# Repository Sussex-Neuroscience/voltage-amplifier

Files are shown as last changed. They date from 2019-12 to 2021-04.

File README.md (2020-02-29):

# Arduino Due compatible voltage amplifier

Hi! This repository contains all the necessary documents to replicate an arduino Due compatible voltage amplifier.

This system was developed as part of a research project of the [Ward Lab](http://www.sussex.ac.uk/profiles/92444/research). It is to be used with a stimulus isolation adaptor from BIOPAC, more specifically one of the models that provide isolated voltage: https://www.biopac.com/product/stimulus-isolation-adapters/

The idea is simple, we use the true analog output ports from the Arduino DUE as an independent channel and amplify their signals using Operational amplifiers. In this case two [LM741](https://www.biopac.com/product/stimulus-isolation-adapters/) from Texas instruments. Using serial communication the system can be controlled in various ways, from the Arduino IDE to whatever programming languages (Python, Matlab, etc).

In [Hardware](./hardware) readers are going to find the information necessary (gerbers, bill of materials) to order components and replicate the board.

In [code](./code) readers are going to find the arduino code needed to for sending serial commands to the arduino and getting voltage signals out of the 2 different analog channels. There is also example code in Matlab to show how to control the arduino (readers should note that the Matlab Arduino libraries are not being used. Just plain serial commands).

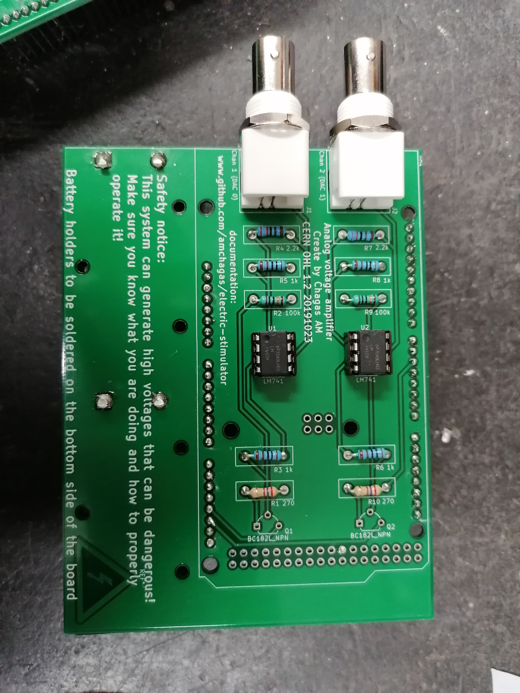
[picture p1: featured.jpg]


---

## setting up system (bare minimum):

1. Install Arduino IDE and its drivers: https://www.arduino.cc/en/Main/Software
2. Install the arduino DUE support (SAM boards) using the board manager tool in the IDE (tools > boards > boards_manager)

3. Download and unzip the serial communication library (https://github.com/kroimon/Arduino-SerialCommand). Place the unzipped folder on the Arduino Libraries folder.

4. test that everything is working by opening the serial communication library example code and uploading it to the board.

  - Emit a couple of commands (eg: ON, OFF, HELLO) using the serial monitor (can be accessed via the icon on the top right corner of the Arduino IDE).

5. Upload the "SerialCommands" sketch to the arduino board and open the Serial monitor

- **channel1**  
    - DUR1 ZZZ sets the stimulus duration in milliseconds (where ZZZ should be replaced by the time desired) for channel 1.    
      - ZZZ specifies the amount of time of ON and OFF phase of the pulse (ie ZZZ=10 defines a pulse that is 10ms on and 10ms off).
    - REP1 WWW sets the number of pulses for channel 1.  
    - AMP1 YYY sets the voltage level, in between 550 and 2750 for channel 1.  
    - GO1 starts the stimulation in channel 1.  

- **channel 2**  
    - DUR2 ZZZ sets the stimulus duration in milliseconds(where ZZZ should be replaced by the time desired) for channel 2.    
      - ZZZ specifies the amount of time of ON and OFF phase of the pulse (ie ZZZ=10 defines a pulse that is 10ms on and 10ms off).    
    - REP2 WWW sets the number of pulses for channel 2.    
    - AMP2 YYY sets the voltage level, in between 550 and 2750 milliVolts for channel 2.    
    - GO2 starts the stimulation in channel 2.    

---

### Hardware considerations:

- The BIOPAC system takes voltage signals as inputs to create the electric stimulus. Here we are using an Arduino DUE as the system needs a true analog voltage and not PWM.
  - The arduno DUE has two DAC ports that output signals in between 0.55 and 2.75V with 12bit resolution (in other words, we can divide the 2.75-0.55 interval into 4096 discrete levels).
  - One limitation is that there is no true 0V for the ports, so we need to use a NPN transistor to interrupt the circuit and realy turn off the system.
  - [Here]((/hardware/transistor_switch/schematic.pdf)) is the diagram for the transistor switches

  ---

### ordering everything using [Kitspace.org](kitspace.org)

- To make it easy for readers to source all necessary components, we've uploaded this project to Kitspace, an open source project that simplifies the ordering process. Follow this link https://kitspace.org/boards/github.com/sussex-neuroscience/voltage-amplifier/ to go to the project page on Kitspace.

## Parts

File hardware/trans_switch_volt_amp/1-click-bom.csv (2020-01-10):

References | Qty | Description | Manufacturer | MPN | Manufacturer_1 | MPN_2 | Manufacturer_3 | MPN_4 | Manufacturer_5 | MPN_6 | Manufacturer_7 | MPN_8 | Digikey | Mouser | RS | Newark | Farnell
R1;R10 | 2 | 270 ohm | RS-pro | 707-7625 |  |  |  |  |  |  |  |  |  |  | 707-7625
R2;R9 | 2 | 100k ohm | TE connectivity | LR1F100k |  |  |  |  |  |  |  |  |  |  | 125-1168
R3;R5;R6;R8 | 4 | 1k ohm | Vishay | MRS25000C1001FCT00 |  |  |  |  |  |  |  |  |  |  | 683-3165
R4;R7 | 2 | 2.2k ohm | Vishay | MRS25000C2201FCT00 |  |  |  |  |  |  |  |  |  |  | 683-3449
J1;J2 | 2 | BNC connector | Amphenol | B6252H5-NPP3G-50 |  |  |  |  |  |  |  |  |  |  | 700-9411
Q1;Q2 | 2 | NPN transistorST |  | BD139 |  |  |  |  |  |  |  |  |  |  | 314-1823
U1;U2 | 2 | IC socket | Assmann | A 08-LC-TT |  |  |  |  |  |  |  |  |  |  | 674-2435
U1;U2 | 2 | LM741 opamp | Texas instruments | LM741CN/NOPB |  |  |  |  |  |  |  |  |  |  | 535-9969
B1;B2 | 2 | Battery clips | Keystone | 1294 |  |  |  |  |  |  |  |  |  |  | 172-5845

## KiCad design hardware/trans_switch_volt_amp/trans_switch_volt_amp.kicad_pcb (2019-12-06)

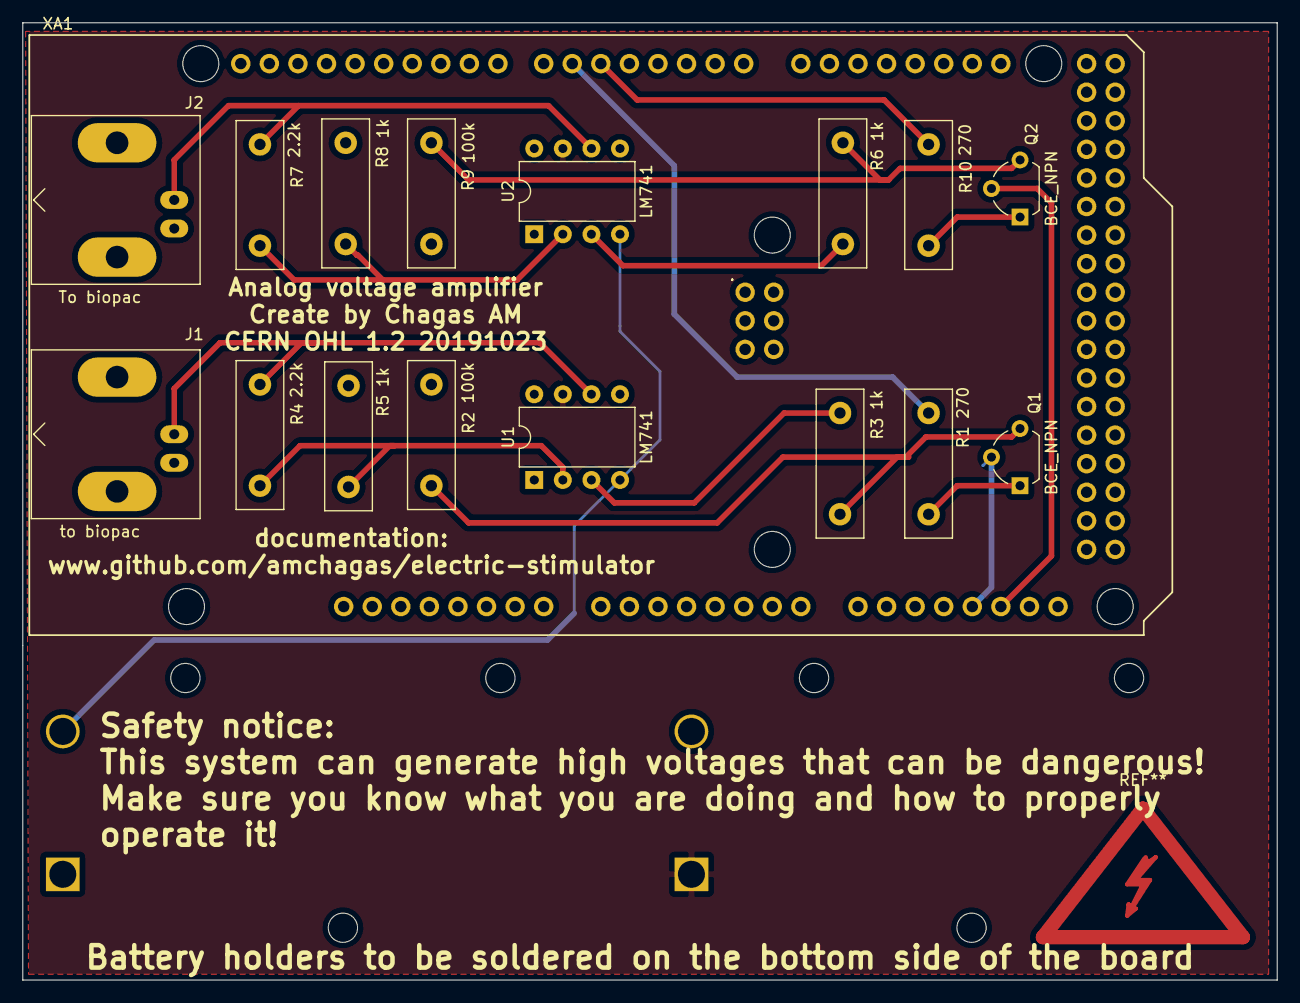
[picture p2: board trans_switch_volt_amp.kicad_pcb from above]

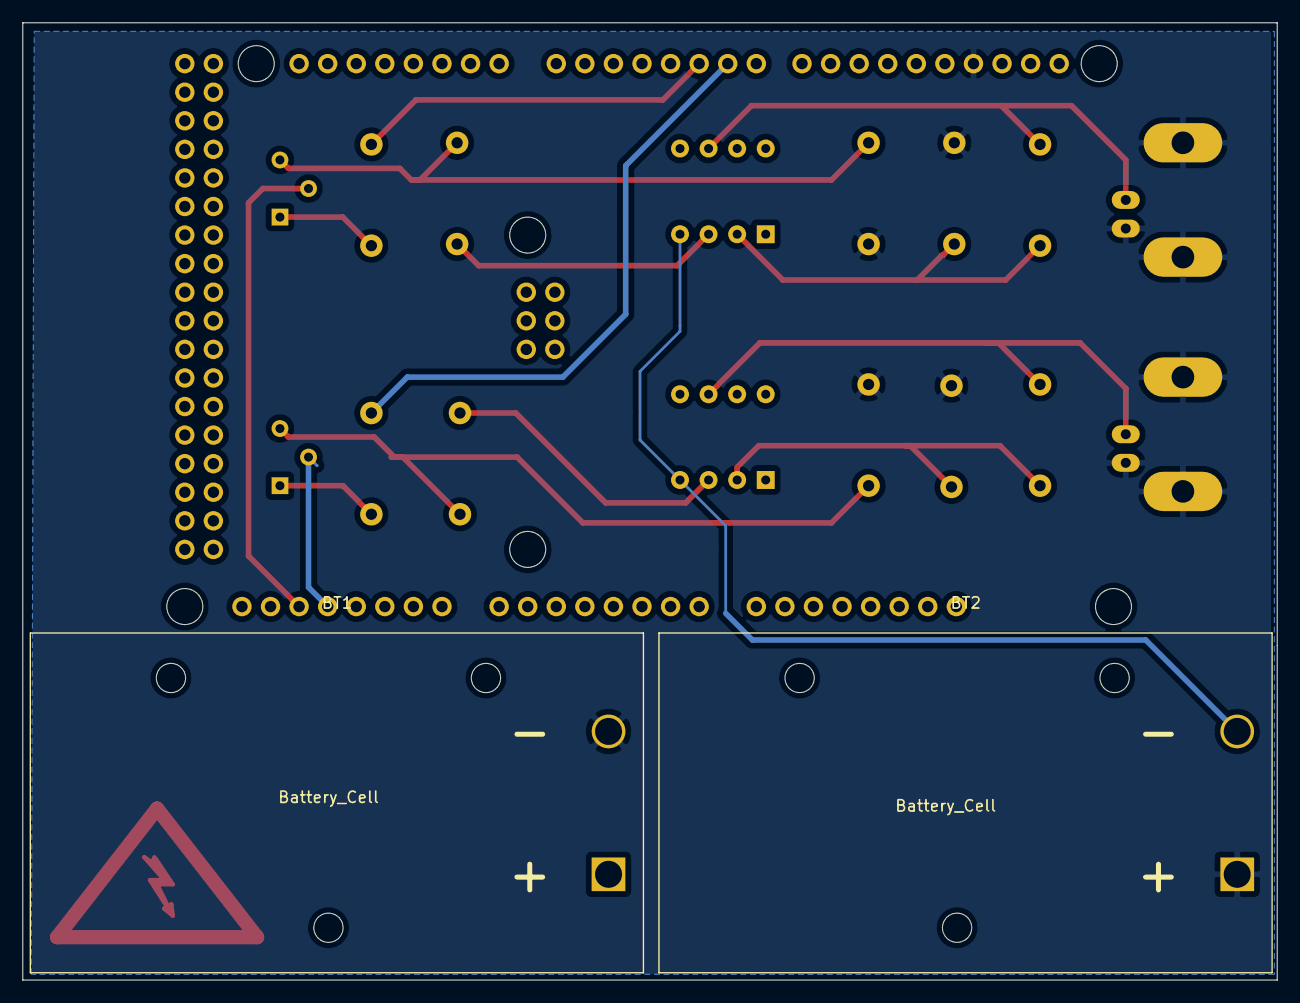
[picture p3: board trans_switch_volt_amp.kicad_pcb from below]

Board: 2 copper layers, 111.5 x 85.1 mm, 19 parts (2 on the bottom side), 17 nets.

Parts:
BT1, BT2: Battery_Cell; BatteryHolder_Eagle_12BH611-GR
J1: to biopac; BNC_Amphenol_B6252HB-NPP3G-50_Horizontal
J2: To biopac; BNC_Amphenol_B6252HB-NPP3G-50_Horizontal
Q1, Q2: BCE_NPN; TO-92L_Wide
R1, R10: 270; R_Box_L13.0mm_W4.0mm_P9.00mm
R2, R9: 100k; R_Box_L13.0mm_W4.0mm_P9.00mm
R3, R5, R6, R8: 1k; R_Box_L13.0mm_W4.0mm_P9.00mm
R4, R7: 2.2k; R_Box_L13.0mm_W4.0mm_P9.00mm
U1, U2: LM741; DIP-8_W7.62mm
XA1: Arduino_Due_Shield

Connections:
GND: BT1.2, BT2.1, J1.2, J2.2, R2.2, R5.1, R8.1, R9.2, XA1.GND1
unnamed: BT1.1, U1.7, U2.7
unnamed: BT2.2, U1.4, U2.4
unnamed: J1.1, R4.2, U1.6
unnamed: J2.1, R7.2, U2.6
unnamed: Q1.1, R1.1
unnamed: Q1.2, XA1.DAC0
unnamed: Q1.3, R2.1, R3.1
unnamed: Q2.1, R10.1
unnamed: Q2.2, XA1.DAC1
unnamed: Q2.3, R6.1, R9.1
unnamed: R1.2, XA1.D6
unnamed: R3.2, U1.3
unnamed: R4.1, R5.2, U1.2
unnamed: R6.2, U2.3
unnamed: R7.1, R8.2, U2.2
unnamed: R10.2, XA1.D5

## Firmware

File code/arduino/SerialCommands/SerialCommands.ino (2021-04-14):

// Code to set and start electrical stimulation using an Arduino DUE and BIOPAC system
// CC BY SA 4.0 20190924
// Chagas AM.
// 
// Based on Demo Code for SerialCommand Library by Steven Cogswell May 2011

#include <SerialCommand.h>

#define arduinoLED 13   // Arduino LED on board

// channel 1
int transistorPort1 = 6;
long int stimDur1 = 0;
float stimAmp1 = 550;
int mappedOut1 = 0;
int numRep1 = 1;
int DACport1 = DAC0;

// channel 2
int transistorPort2 = 5;
long int stimDur2 = 0;
float stimAmp2 = 550;
int mappedOut2 = 0;
int numRep2 = 1;
int DACport2 = DAC1;

SerialCommand sCmd;     // The demo SerialCommand object

void setup() {
  pinMode(arduinoLED, OUTPUT);      // Configure the onboard LED for output
  pinMode(transistorPort1,OUTPUT); // configure transistor port
  pinMode(transistorPort2,OUTPUT); // configure transistor port
  pinMode (DACport1,OUTPUT);
  pinMode (DACport2,OUTPUT);
  digitalWrite(arduinoLED, LOW);    // default to LED off
  analogWriteResolution(12);         // set the resolution to 12, since we are using the DAC ports

  Serial.begin(9600);

  // Setup callbacks for SerialCommand commands
  sCmd.addCommand("ON",    LED_on);          // Turns LED on
  sCmd.addCommand("OFF",   LED_off);         // Turns LED off

  sCmd.addCommand("DUR1",   duration1);        // stimulus duration (milliseconds) channel 1
  sCmd.addCommand("AMP1",   amplitude1);       // stimulus amplitude (volts) channel 1
  sCmd.addCommand("REP1",   repetitions1);       // nuber of trains channel 1
  sCmd.addCommand("GO1",    stim_on1);         // Start stimulation channel 1
  sCmd.addCommand("DUR2",   duration2);        // stimulus duration (milliseconds) channel 2
  sCmd.addCommand("AMP2",   amplitude2);       // stimulus amplitude (volts) channel 2
  sCmd.addCommand("REP2",   repetitions2);       // nuber of trains channel 2
  sCmd.addCommand("GO2",    stim_on2);         // Start stimulation channel 2

  sCmd.addCommand("HELLO", sayHello);        // Echos the string argument back
  sCmd.addCommand("P",     processCommand);  // Converts two arguments to integers and echos them back
  sCmd.setDefaultHandler(unrecognized);      // Handler for command that isn't matched  (says "What?")
  Serial.println("Ready");
}

void loop() {
  sCmd.readSerial();     // We don't do much, just process serial commands
}


void LED_on() {
  Serial.println("LED on");
  digitalWrite(arduinoLED, HIGH);
}

void LED_off() {
  Serial.println("LED off");
  digitalWrite(arduinoLED, LOW);
}

void stim_on1() {
  Serial.println("Stimulus settings channel 1:");
  Serial.print("Duration "); Serial.print(stimDur1); Serial.println(" microsseconds");
  Serial.print("Analog output "); Serial.print(stimAmp1); Serial.println(" millivolts");
  Serial.print("number of trains "); Serial.println(numRep1);
  Serial.println("stim on");



  // we need to map the voltage level to integer in between 0 and 4095)but map function only takes integers,
  // so we make sure our floats are integers (analog output has a range between 0.55 to 2.75, we multiply that
  // by 100 as well as the stimAmp value)
  mappedOut1 = map(stimAmp1, 550, 2750, 0, 4095);

  for (int i=0; i <= numRep1; i++){
    digitalWrite(arduinoLED, HIGH);
    digitalWrite(transistorPort1, HIGH);
    //Serial.println(mappedOut1);
    analogWrite(DACport1,mappedOut1);
    delayMicroseconds(stimDur1);
    //delay(stimDur1);
    analogWrite(DACport1,0);
    digitalWrite(arduinoLED, LOW);
    digitalWrite(transistorPort1, LOW);
    delayMicroseconds(stimDur1);
    //delay(stimDur1);
  }// end for
  Serial.println("stim off");

}

void stim_on2() {
  Serial.println("Stimulus settings channel 2:");
  Serial.print("Duration "); Serial.print(stimDur2); Serial.println(" microsseconds");
  Serial.print("Analog output "); Serial.print(stimAmp2); Serial.println(" millivolts");
  Serial.print("number of trains "); Serial.println(numRep2);
  Serial.println("stim on");



  // we need to map the voltage level to integer in between 0 and 4095)but map function only takes integers,
  // so we make sure our floats are integers (analog output has a range between 0.55 to 2.75, we multiply that
  // by 100 as well as the stimAmp value)
  
  mappedOut2 = map(stimAmp2, 550, 2750, 0, 4095);

  for (int i=0; i <= numRep2; i++){
    digitalWrite(arduinoLED, HIGH);
    digitalWrite(transistorPort2, HIGH);
    analogWrite(DACport2,mappedOut2);
    //delay(stimDur2);
    delayMicroseconds(stimDur2);
    analogWrite(DACport2,0);
    digitalWrite(arduinoLED, LOW);
    digitalWrite(transistorPort2, LOW);
    //delay(stimDur2);
    delayMicroseconds(stimDur2);
  }// end for
  Serial.println("stim off");

}




void repetitions1() {
  char *arg;
  int aNumber;

  arg = sCmd.next();    // Get the next argument from the SerialCommand object buffer
  if (arg != NULL) {    // As long as it existed, take it
    Serial.print("number of trains channel 1: ");
    Serial.print(arg);

    aNumber = atoi(arg);    // Converts a char string to an integer
    numRep1 = aNumber;
  }
  else {
    Serial.println("repetitions = 0!, defaulting it to 1!");
    numRep1 = 1;
  }
}

void repetitions2() {
  char *arg;
  int aNumber;

  arg = sCmd.next();    // Get the next argument from the SerialCommand object buffer
  if (arg != NULL) {    // As long as it existed, take it
    Serial.print("number of trains channel 2: ");
    Serial.print(arg);

    aNumber = atoi(arg);    // Converts a char string to an integer
    numRep2 = aNumber;
  }
  else {
    Serial.println("repetitions = 0!, defaulting it to 1!");
    numRep2 = 1;
  }
}

void duration1() {
  char *arg;
  long int aNumber;

  arg = sCmd.next();    // Get the next argument from the SerialCommand object buffer
  if (arg != NULL) {    // As long as it existed, take it
    Serial.print("stim duration channel 1 ");
    Serial.print(arg);
    Serial.println(" milliseconds");
    aNumber = atoi(arg);    // Converts a char string to an integer
    stimDur1 = aNumber;
  }
  else {
    Serial.println("no duration given!, defaulting it to zero!");
    stimDur1 = 0;
  }
}

void duration2() {
  char *arg;
  long int aNumber;

  arg = sCmd.next();    // Get the next argument from the SerialCommand object buffer
  if (arg != NULL) {    // As long as it existed, take it
    Serial.print("stim duration channel 2 ");
    Serial.print(arg);
    Serial.println(" milliseconds");
    aNumber = atoi(arg);    // Converts a char string to an integer
    stimDur2 = aNumber;
  }
  else {
    Serial.println("no duration given!, defaulting it to zero!");
    stimDur2 = 0;
  }
}

void amplitude1() {
  char *arg;
  float aNumber;

  arg = sCmd.next();    // Get the next argument from the SerialCommand object buffer
  if (arg != NULL) {    // As long as it existed, take it
    Serial.print("stim amplitude channel 1");
    Serial.println(arg);
    aNumber = atoi(arg);    // Converts a char string to an float
    if (aNumber<550){
      Serial.println("defaulting to minimum amplitude 0.55");
      aNumber = 550;
      }//if number smaller than 550

    if (aNumber>2750){
      Serial.println("defaulting to maximum amplitude 2750");
      aNumber = 2750;
      }//if number bigger than 2750

    stimAmp1 = aNumber;
  }
  else {
    Serial.println("no amplitude given!, defaulting it to zero!");
    stimAmp1 = 0;
  }
}

void amplitude2() {
  char *arg;
  float aNumber;

  arg = sCmd.next();    // Get the next argument from the SerialCommand object buffer
  if (arg != NULL) {    // As long as it existed, take it
    Serial.print("stim amplitude channel 2");
    Serial.println(arg);
    aNumber = atoi(arg);    // Converts a char string to an float
    if (aNumber<550){
      Serial.println("defaulting to minimum amplitude 550");
      aNumber = 550;
      }//if number smaller than 0.55

    if (aNumber>2750){
      Serial.println("defaulting to maximum amplitude 2750");
      aNumber = 2750;
      }//if number bigger than 2.75

    stimAmp2 = aNumber;
  }
  else {
    Serial.println("no amplitude given!, defaulting it to zero!");
    stimAmp2 = 0;
  }
}

void processCommand() {
  int aNumber;
  char *arg;

  Serial.println("We're in processCommand");
  arg = sCmd.next();
  if (arg != NULL) {
    aNumber = atoi(arg);    // Converts a char string to an integer
    Serial.print("First argument was: ");
    Serial.println(aNumber);
  }
  else {
    Serial.println("No arguments");
  }

  arg = sCmd.next();
  if (arg != NULL) {
    aNumber = atol(arg);
    Serial.print("Second argument was: ");
    Serial.println(aNumber);
  }
  else {
    Serial.println("No second argument");
  }
}

// This gets set as the default handler, and gets called when no other command matches.
void unrecognized(const char *command) {
  Serial.println("What?");
}

void sayHello() {
  char *arg;
  arg = sCmd.next();    // Get the next argument from the SerialCommand object buffer
  if (arg != NULL) {    // As long as it existed, take it
    Serial.print("Hello ");
    Serial.println(arg);
  }
  else {
    Serial.println("Hello, whoever you are");
  }
}

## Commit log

2019-09-22 to communicate with the arduino, we are using a serial library
    This library sets a token system and we implemented functions for the
    Python side of things to wait for a confirmation token.
2019-09-24 Updated documentation and electronics schematics
    [transistor_switch.kicad_pcb, transistor_switch.sch]
2019-10-07 updated arduino code so that it can trigger two channels
2019-10-07 add matlab code to communicate with Arduino
2019-10-07 updated electronic schematics, exported schematics pdf and made a commented photo of the protoboard
    [transistor_switch.sch]
2019-10-16 update code on arduino and matlab due to latest testing. Small changes to serial port used
2019-10-16 schematics for 2 channel voltage amplifier
    [voltage_amplifier.kicad_pcb, voltage_amplifier.sch]
2019-10-16 start on implementing an arduino shield for the stimulator
    [trans_switch_volt_amp.kicad_pcb, trans_switch_volt_amp.sch]
2019-10-21 created shield for the amplifier system
    [trans_switch_volt_amp.kicad_pcb, trans_switch_volt_amp.sch]
2019-10-23 finish writing warnings and lincenses on the board
    [trans_switch_volt_amp-B_Adhes.gbr, trans_switch_volt_amp-B_CrtYd.gbr, trans_switch_volt_amp-B_Cu.gbr, trans_switch_volt_amp-B_Fab.gbr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]
2019-11-07 start BOM
    [BOM.ods]
2019-11-25 start writing down the BOM for the electric stimulator
    [BOM.ods]
2019-11-27 clean up repository and add 1-click-bom.csv
    [1-click-bom.csv, BOM.ods, trans_switch_volt_amp.sch, voltage_amplifier.kicad_pcb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]
2019-12-06 update board and fixed transistor bug
    [trans_switch_volt_amp.kicad_pcb, trans_switch_volt_amp.sch]
2020-01-10 remove old version of board
    [transistor_switch.kicad_pcb, transistor_switch.sch]
2020-01-10 update bom
    [1-click-bom.csv]
2020-01-10 update arduino code so that input in in mV.
2020-01-10 update arduino code so that input in is mV. and update matlab code
2020-01-10 update readme with information that voltage should be given in millivolts
2020-01-10 organize location of resistor indicators
    [trans_switch_volt_amp.sch]
2021-04-14 a bit of housekeeping, changing durations to microsseconds and voltages to millivolts. Correcting map function

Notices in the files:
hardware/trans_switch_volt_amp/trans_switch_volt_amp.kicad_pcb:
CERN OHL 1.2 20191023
